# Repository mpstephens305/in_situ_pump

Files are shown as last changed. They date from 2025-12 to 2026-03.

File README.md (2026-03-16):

# in_situ_pump
```diff
-This site is actively under construction and will be fully functional in March, 2026. 
```
<P>A low cost, open source in situ pump for marine and freshwater sampling being developed at Florida International University by Mark Stephens and Andres Martinez.</P>

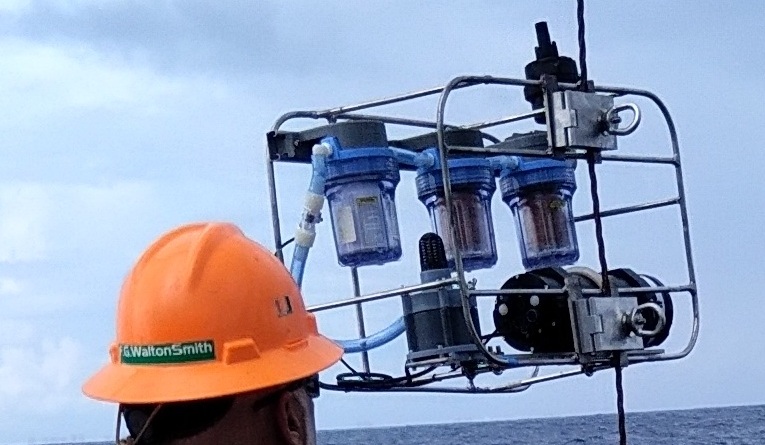
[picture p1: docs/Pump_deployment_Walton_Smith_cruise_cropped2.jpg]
Pump deployment aboard RV Walton Smith in October 2025


<P><b>Motivation: </b>In situ pumps allow for simultaneous sampling at multiple depths. However, commercially available units can cost tens of thousands of dollars. For applications involving shallow deployments, a more feasible solution is desirable. Our intention is to provide a complete step-by-step guide for building, programming, and operating the in_situ_pump. The system is adaptable for use in a variety of environments and projects. Community input and collaborations are most welcome. 
</P>

## Features
* 3D printed pump unit driven by a [Blue Robotics subsea motor](https://bluerobotics.com/store/thrusters/t100-t200-thrusters/m200-motor/).
* Controlled by a [Teensy 4.1](https://www.pjrc.com/store/teensy41.html) development board.
* Electronics and power supply inside watertight enclosure.
* Adaptable to various filter media (cartridges, GFF, acrylic fiber, etc.).
* Adaptable to sampling different chemical and isotopic species in the dissolved and particulate phases in seawater and freshwater.
* Simple operation.
* Easily programmable start delay, sampling duration, and motor speed.

## Fact Sheet:
* Materials cost: ~$2000 US.
* Power supply: c-cell batteries (can be adapted to other batteries including lithium).
* Maximum depth: 300 m.
* Sensors: pressure (depth), temperature, flow rate, voltage, DC current.
* Data storage: microSD card.
* Communications: USB.
* Dimensions: 24 x 18 x 12 in.
* Weight: 40 lb.

## How to Get One

### Hardware
<table>
<TR>
<TD>
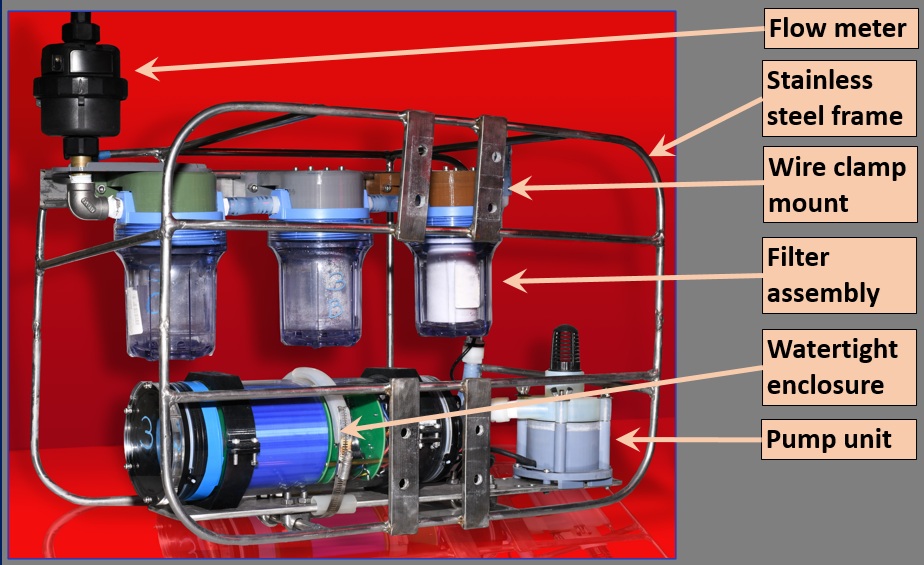
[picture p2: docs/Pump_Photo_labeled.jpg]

	
For step-by-step build instructions for each component, use the following links: <a href="hardware/frame_assembly/frame_assembly.md">frame_assembly</a>, 
<a href="hardware/pump_unit/pump_unit.md">pump_unit_assembly</a>, <a href="hardware/electronics_assembly/electronics_assembly.md">electronics_assembly</a> (including the <a href="hardware/electronics_assembly/pcb_mainboard.md">pcb mainboard_assembly</a> and the <a href="hardware/electronics_assembly/battery_holder_assembly.md">battery_holder_assembly</a>), and the <a href="hardware/filter_holder_assembly/filter_holder_assembly.md">filter_holder_assembly</a>. In addition, we provide CAD files for manufacture of the <a href="hardware/wire_clamp/wire_clamp.md">wire_clamp_assembly</a>. 
</td></tr></table>

### Software
<table width="100%">
	<thead>
    <tr>
      <th width="40%" valign="top"><P>Pump operation is controlled by the Arduino sketch <a href="software/teensy_pump_simple.ino">teensy_pump_simple.ino</P></a>.</P> 
<P>Prior to deployment, the user specifies the pump delay, pump duration, motor speed, and data filename. At the start of a deployment, the program is initialized, and then the countdown to pump start up (i.e., pump delay) begins. The motor then spins up and operates for the specified pump duration.  See the flowchart at the right for the full sequence.</P>
<P>Our step-by-step <a href="software/Software.md">guide</a> includes instructions for software installation, operation, and data recovery.</P>
</th>
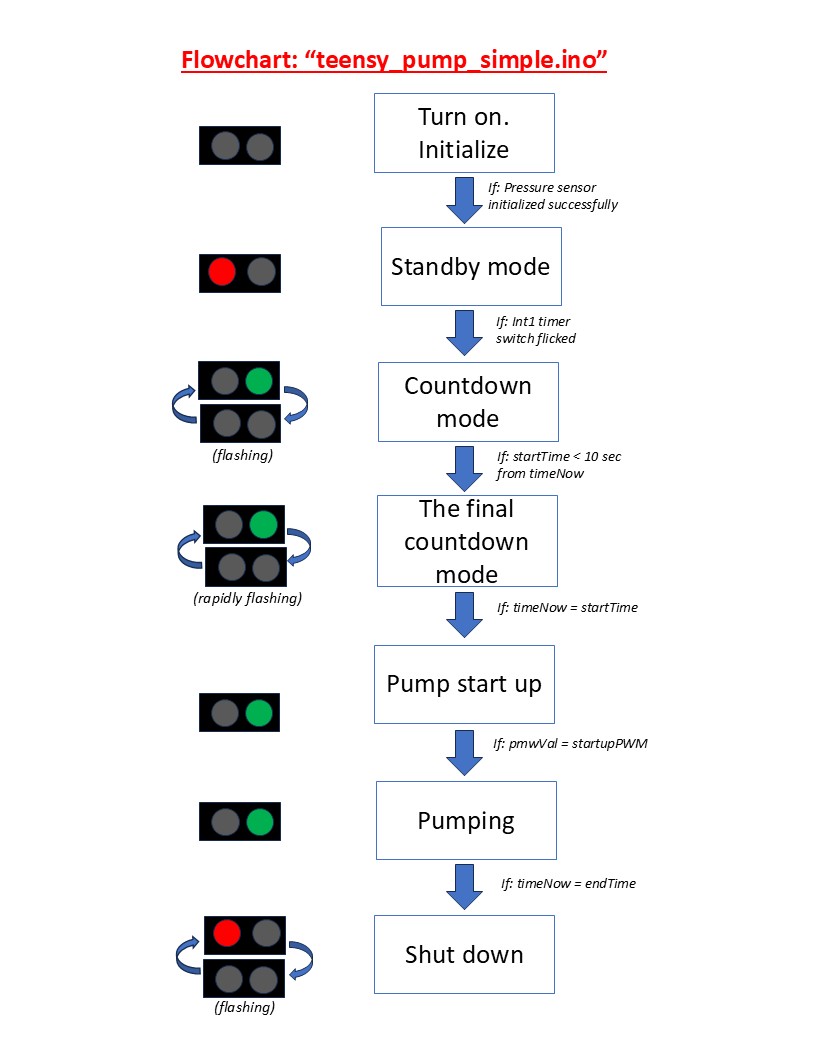
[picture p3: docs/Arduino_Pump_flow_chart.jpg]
      <th width="60%"></th>
    </tr>
  </thead>

</table>

## Deployments

### South Florida Test Cruise
The first ever deployments of the in_situ_pump were conducted in the Gulf Stream offshore South Florida and the Florida Keys on a cruise aboard R/V Walton Smith, October 7-9, 2025. Additional cruises are planned for 2026 in the Sargasso Sea.

<p>A few issues were identified during the this cruise. First, we found that on some deployments the microcontroller repeatedly shut down and rebooted. We identified the issue: the unit was losing power when it swung on the hydrowire during deployment because the springs in the battery compartment were too weak. So, we replaced them with more robust springs.  Second, there were two instances where the outlet of the pump head fractured. In order to address this, we are now using a tougher resin to print these parts. And third, the extraction efficiency of Be-7 from seawater was lower than expected.  In order to address this we are conducting tests using different flow rates and larger masses of filtering material. Additionally, we observed that some of the filter cartridges did not fit snuggly against the filter holders, allowing some of pumped seawater to bypass the filtering material. To address this, we replaced the included gaskets with more robust gaskets of our own design.
	
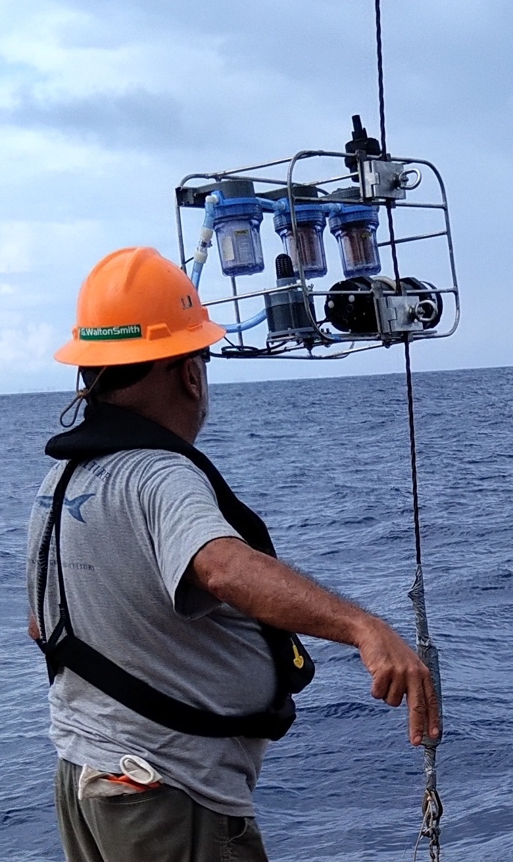
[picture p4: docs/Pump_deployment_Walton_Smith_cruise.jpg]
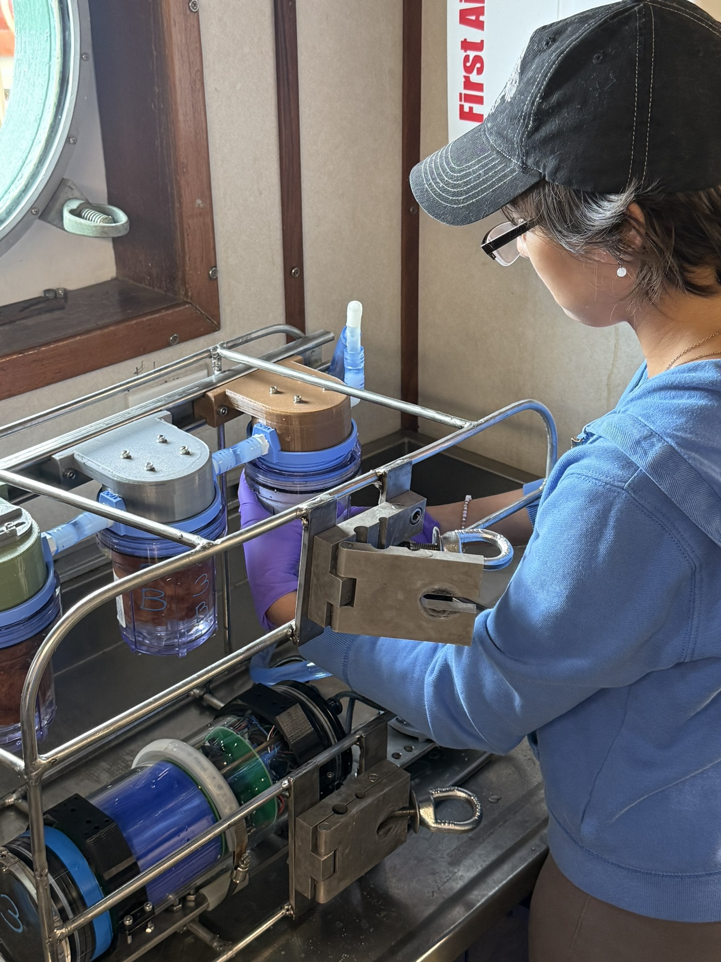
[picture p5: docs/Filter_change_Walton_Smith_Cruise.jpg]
 |  

## Presentations & Publications

### AGU25, New Orleans, 11-19 December 2025

<P>The in_situ_pump was introduced through a poster presentation in <a href="https://macgyver-sessions.github.io/">The MacGyver Sessions</a> at AGU's Annual Meeting. The poster can be accessed via <a href="https://zenodo.org/records/18157174">The MacGyver Sessions Zenodo site</a> as well as on the <a href="https://doi.org/10.22541/essoar.176662276.61585030/v1">ESS Open Archive</a>.

## Acknowledgements
*This project is supported by the U.S.National Science Foundation (Grant # NSF-OCE-2446521). We are grateful for technical support and advice provided at Florida International University's Applied Research Center (FIU-ARC) from the following individuals: Dr Yipeng He, Theophile Pierre, Gabriel Cerioni, and Anthony Abrahao.  Emily Jackson and Sahaira Paz assisted with testing the device and operations on the South Florida cruise. We thank the captain and crew of research vessel F.G. Walton Smith. Photo credits: Emily Jackson and Clint Miller.*

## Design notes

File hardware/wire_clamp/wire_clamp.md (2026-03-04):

# wire_clamp_assembly 

<P>Two wire clamps are used to attach the frame to the hydro wire for deployment.  The book 
clamp design consists of an upper and lower plate that are hinged using a stainless-steel dowel.  
Clamping force is applied by rotating the eye nut onto the threaded rod end bolt.  The design 
includes grooves for two wire sizes.  The dimensions of the clamp body are 3 
x 4.5 x 1.25 inches.  The clamps are attached to the wire clamp mounts on the frame with four 
3/8”-16 stainless steel socket head screws and hex nuts.

<table>
<tr>
<td width="50%">
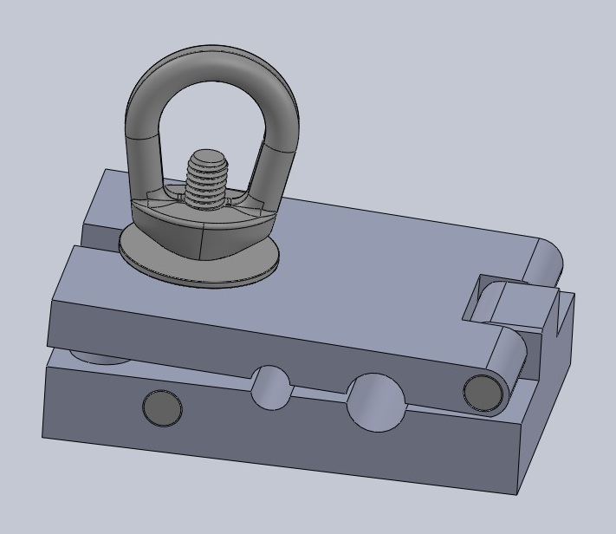
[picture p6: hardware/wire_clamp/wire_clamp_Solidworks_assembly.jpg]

</td>
<td width="50%">
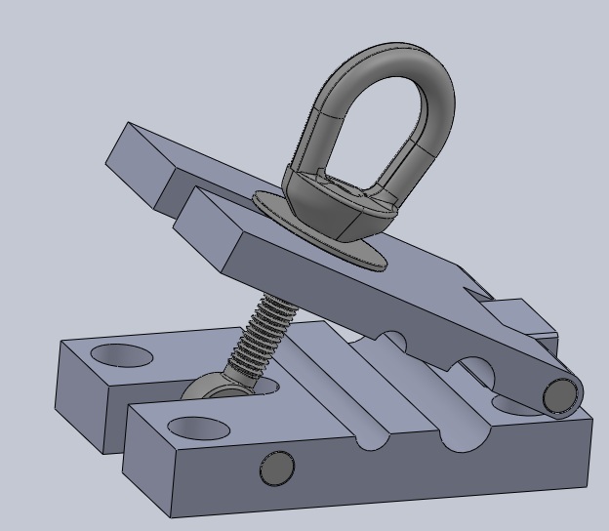
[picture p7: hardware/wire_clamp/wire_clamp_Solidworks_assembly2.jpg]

</td>
</tr>

<tr>
<td colspan=2 align=center>
wire_clamp, Solidworks assembly view
<P>The 3D models including Solidworks parts and assembly are available in the <a href="3D_models/">wire_clamp 3D Models directory</a>.
</td>
</tr>
</table>

<P>
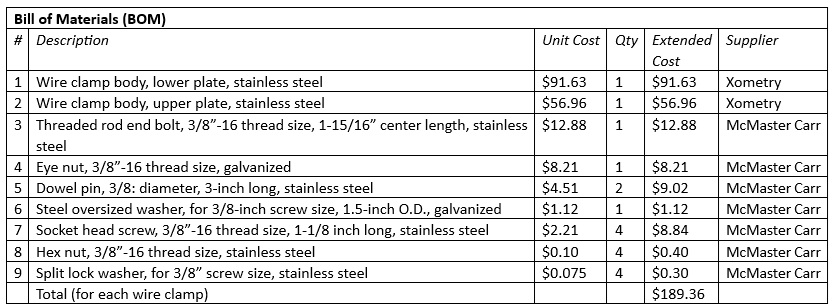
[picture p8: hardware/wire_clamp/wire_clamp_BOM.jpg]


### Assembly (approximate time: 10 minutes):  
1. Attach the lower plate to the wire clamp mounting plates on the frame using four socket head screws, 
hex nuts, and split lock washers. 
2. Attach the upper plate to the lower plate using a stainless-steel dowel. 
3. Attach the threaded rod end bolt to the lower plate using a stainless-steel dowel. 
4.  Place the oversized steel washer and eye bolt onto the threaded rod end bolt. 

### CAD drawings (dimensions in inches):

<table>
<tr>
<td>
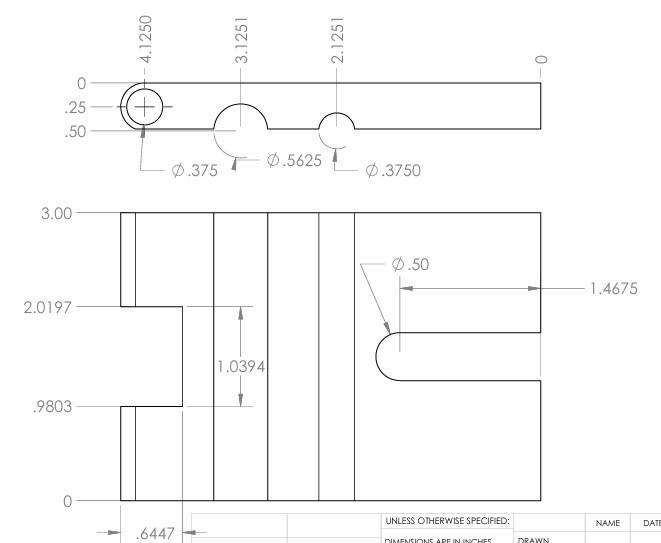
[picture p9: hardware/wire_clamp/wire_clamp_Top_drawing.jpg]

</td>
</tr>
<tr>
<td align=center>
Upper Plate
</td>
</tr>
</table>

<table>
<tr>
<td>
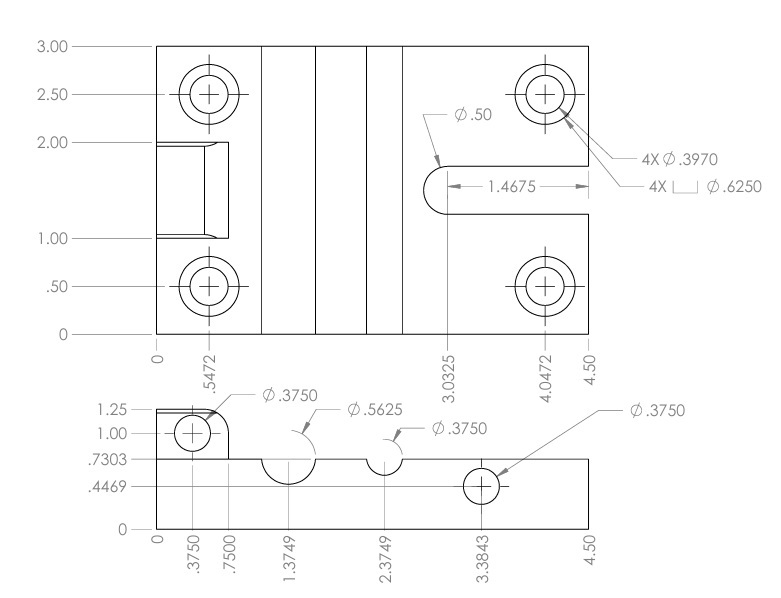
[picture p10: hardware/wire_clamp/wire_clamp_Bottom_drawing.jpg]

</td>
</tr>
<tr>
<td align=center>
Lower Plate
</td>
</tr>
</table>

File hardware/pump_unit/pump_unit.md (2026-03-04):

# pump_unit_assembly
 	 
<P>The pump_unit_assembly consists of a <a href="https://bluerobotics.com/store/thrusters/t100-t200-thrusters/m200-motor/">Blue Robotics M200 subsea motor</a> and 3D printed pump components (<I>pump_base</I>, <I>pump_body</I>, <I>pump_impeller</I>, and <i>pump_head</i>).  The motor is powered by the 14-cell battery pack and controlled by <a href="https://www.pjrc.com/store/teensy41.html">Teensy 4.1</a> via the <a href="https://bluerobotics.com/store/thrusters/speed-controllers/besc30-r3/">Blue Robotics Basic ESC</a>, all of which are contained within the watertight enclosure.  A <a href="https://bluerobotics.com/store/cables-connectors/penetrators/wlp-vp/?attribute_bulkhead-size-seal-size-plug-compression-compatible-cable-diameter=M10+-+6.5+mm+-+LC+-+6.5+mm+%C2%B1+0.3+mm">Blue Robotics WetLink Penetrator</a> links the external motor with the internal power source.  The pump_unit is secured to the frame_baseplate with four M4 stainless steel screws.

<table>
<tr>
<td width=305>
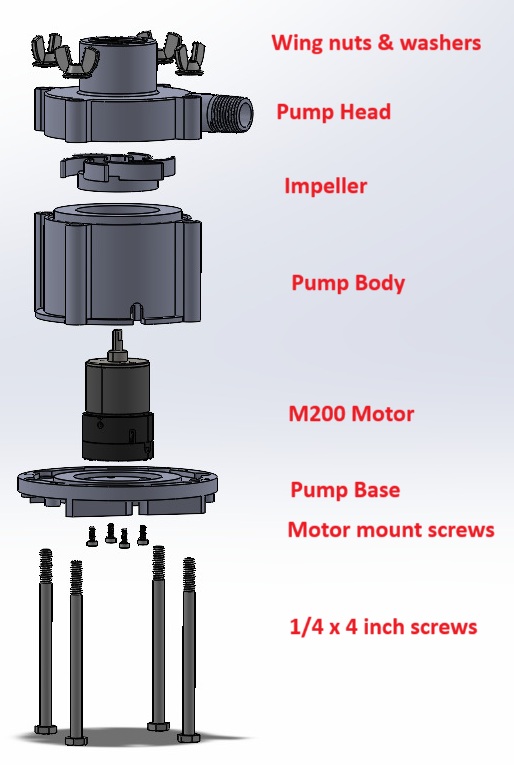
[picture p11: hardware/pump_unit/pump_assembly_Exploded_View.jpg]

</td>
<td width=455>
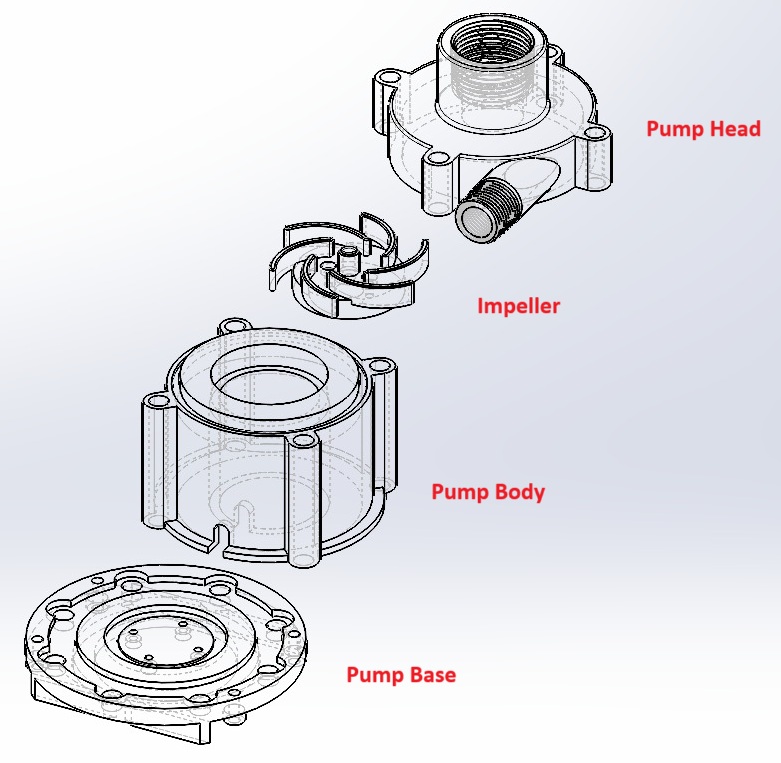
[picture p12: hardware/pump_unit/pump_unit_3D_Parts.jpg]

</td>
</tr>

<tr>
<td align=center>
pump_unit - Exploded View</br>
(Not shown: power cord, strainer, impeller screws, & O-ring)
</td>
<td align=center valign=top>
pump_unit 3D Printed Parts
</td>
</tr>
</table>

<P>
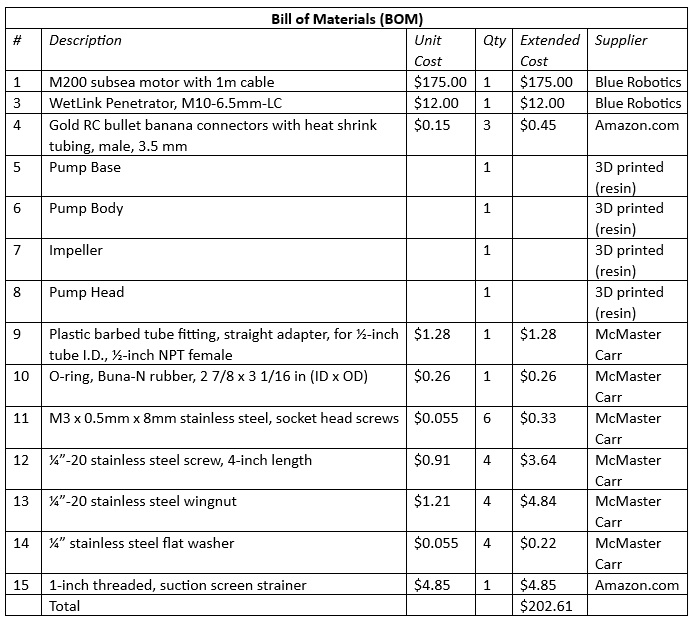
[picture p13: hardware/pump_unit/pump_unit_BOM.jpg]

</P>

### Assembly (approximate time: 20 minutes):  
1. Assemble the WetLink Penetrator with the motor cable following the instructions on the 
Blue Robotics website. 
2. Solder the banana connectors to the three conductors of the motor cable.  Then apply 
heat shrink tubing to the connections. 
3. Attach the motor to pump_base with four M3 x 8mm screws. 
4. Place the pump_body over the motor. 
5. Attach pump_impeller to motor with two M3 x 8mm screws. 
6. Insert O-ring into groove in pump_body. 
7. Seat the pump_head over the pump_impeller and onto pump_body. 
8. Secure pump_head to pump_base with four sets of ¼ inch screws, washers, and 
wingnuts.
9. Screw the 1-inch threaded suction screen strainer into the pump inlet and the 1/2-inch tube fitting onto the outlet.
<table>
<tr>
<td>
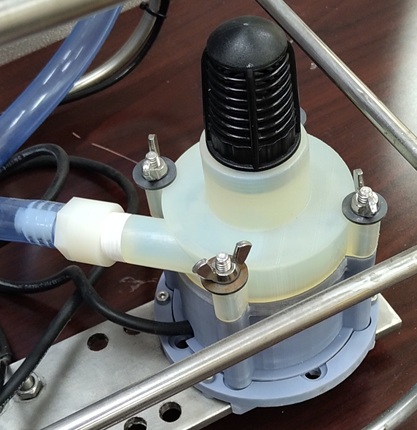
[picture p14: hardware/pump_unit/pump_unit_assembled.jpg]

</td>
</tr>
 <tr>
<td>
Fully assembled pump_unit.
</td>
</tr>
</table>

### 3D Printed Parts
We use a resin printer to produce the pump_unit parts. We have also had success using water resistant filaments, such as PETG, with 100% infill.

The 3D models including .STEP and .STL files are available in the <a href="3D_Models/">3D Models directory</a>.

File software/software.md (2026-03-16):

# software

Given below are step-by-step instructions for A) installing the required software, B) pump operation, and C) data retrieval.

## Installation Instructions

### Step 1: Install *Arduino IDE*
To write the code and upload it to the Teensy 4.1, you will have to use a free software called
Arduino Integrated Development Environment (*Arduino IDE*).
1. Visit https://www.arduino.cc/en/software/ and scroll down until you see Arduino IDE and
download the latest release.
2. Once download finishes, right-click on the file and select “run as administrator”.
3. Follow the pop-ups and select your preferences, then click install.
4. Once installed, open the application.

### Step 2: Install required libraries
To be able to program different components which will be used in the pump, we will need to
install various libraries, Teensyduino to be able to code onto the Teensy board, BlueRobotics
MS5837 Library for the Bar30 pressure sensor, and MTP_Teensy to download the data log after
a run. All the steps below are to be done through the Arduino IDE application.
1. To install Teensyduino, navigate to Files and select preferences.
2. Once the preferences window pops up, you may need to scroll down to even if no
scrollbar appears, in "Additional boards manager URLs" copy the link below then click
OK:
https://www.pjrc.com/teensy/package_teensy_index.json
3. Go back to the main Arduino window and select Boards Manager on the left side.
4. 4. Search Teensy and click install. Now you have the necessary library to operate on the
Teensy.
5. To install the Bar30 pressure sensor library, select Library Manager.
6. 6. Search “BlueRobotics MS5837”.
7. Click install.
8. To install the MTP_Teensy library, visit the link below:
https://github.com/KurtE/MTP_Teensy
9. Click on the green “Code” button and select “Download ZIP”.
10. Once the ZIP file has been downloaded, open your file explorer.
11. Copy the MTP_Teensy file into your Arduino > libraries folder.

### Step 3: Upload Code
The code to run the pump is provided in a .ino file to open on Arduino IDE and upload to the
board. To find this file, go to the GitHub repository, click on the software folder and download
the teensy_pump_simple.ino file. After downloaded, follow the steps below to upload.
1. Connect the cobalt series bulkhead 4-pin cable to the connector on the water tight
enclosure end cap.
2. Open the .ino file with the Arduino IDE application.
3. Select the “Tools” tab on the top left corner of the window.
4. Click on “Board” and select Teensy 4.1.
5. In the same “Tools” tab, click on “Port” and select the correct port corresponding to
where the Teensy is connected.
6. Go back to main window and click “Upload” (the arrow pointing to the right on the top
left of the window).

## Pump operation
The Atrduino sketch <a href="teensy_pump_simple.ino">teensy_pump_simple.ino</a> directs the automatic operation of the pump. Prior to deployment, the user  specifies the following variables: startDelay, pumpTime, startupPWM, and data filename. Then, when the program is activated, pumping begins after startDelay (seconds), operates at a speed corresponding to startupPWM (microseconds), and stops after pumpTime (seconds). Data is recorded every minute to filename.dat.

## Data retrieval
Once you have run the pump you can retrieve data and download it to your computer. The data
includes, date, run time, voltage and current usage, gallons pumped, PWM speed, and depth
(meters).
1. Connect Teensy to your computer through the cobalt series bulkhead 4-pin cable.
2. Select “File” on top left and click “Examples”.
3. Scroll down until you find MTP_Teensy and select mtp-test.
4. Once open, select the “Tools” tab and go to “USB Type”.
5. Select “MTP Disk Experimental”

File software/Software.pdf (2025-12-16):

Software

The software consists of a code which is written on the Arduino IDE and then uploaded to the Teensy 4.1 microcontroller. This code has additional libraries which have to be downloaded to operate some of the components like the Teensy and the Bar30 Pressure Sensor.

The purpose of the code is to run the pump autonomously when turned on at a set speed for the preferred period of time. During the run, it will pump water through the three filters and measure the flow rate.

Download Instructions

Step 1: Installing Arduino IDE

To write the code and upload it to the Teensy 4.1, you will have to use a free software called Arduino IDE.

1. Visit https://www.arduino.cc/en/software/ and scroll down until you see Arduino IDE and download the latest release.
2. Once download finishes, right-click on the file and select “run as administrator”.
3. Follow the pop-ups and select your preferences, then click install.
4. Once installed, open the application.
Step 2: Install required libraries

To be able to program different components which will be used in the pump, we will need to install various libraries, Teensyduino to be able to code onto the Teensy board, BlueRobotics MS5837 Library for the Bar30 pressure sensor, and MTP_Teensy to download the data log after a run. All the steps below are to be done through the Arduino IDE application.

1. To install Teensyduino, navigate to Files and select preferences.
2. Once the preferences window pops up, you may need to scroll down to even if no scrollbar appears, in "Additional boards manager URLs" copy the link below then click OK:
https://www.pjrc.com/teensy/package_teensy_index.json
3. Go back to the main Arduino window and select Boards Manager on the left side.

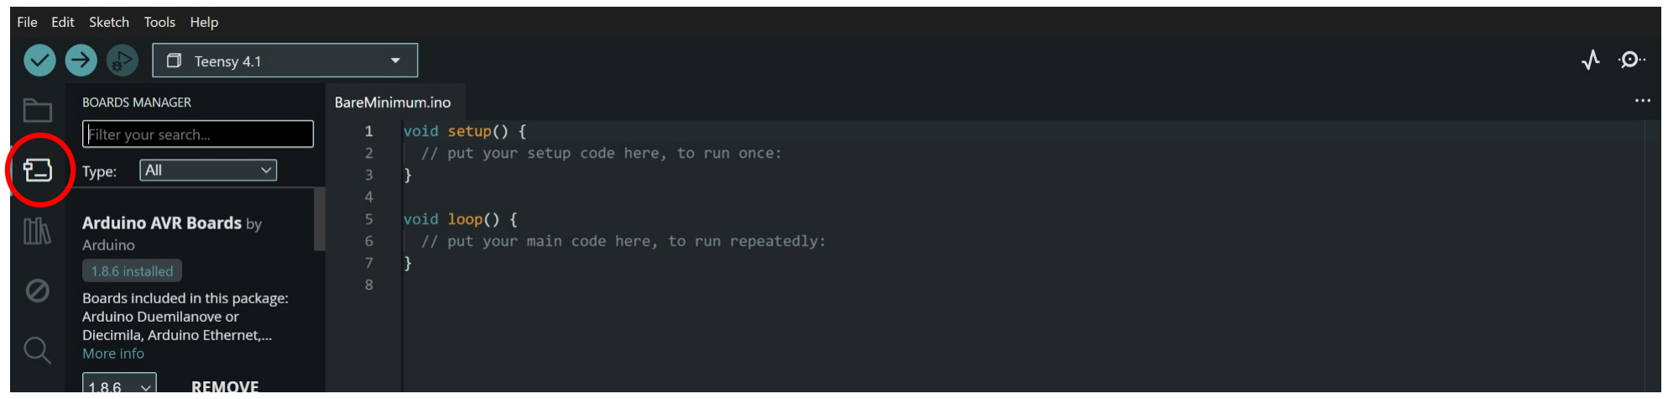
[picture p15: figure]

4. Search Teensy and click install. Now you have the necessary library to operate on the Teensy.
5. To install the Bar30 pressure sensor library, select Library Manager.

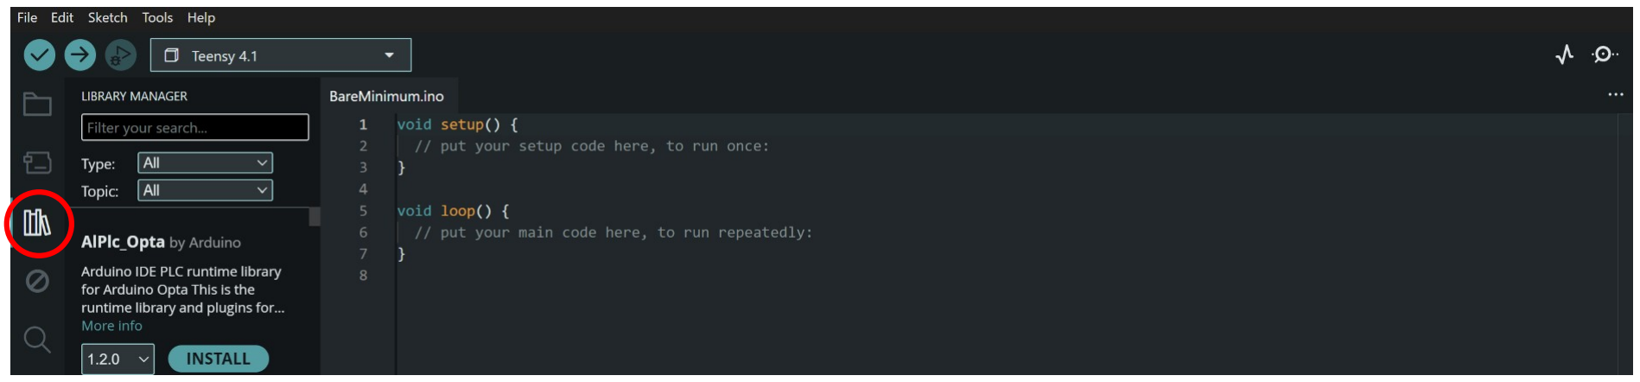
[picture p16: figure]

6. Search “BlueRobotics MS5837”.
7. Click install.
8. To install the MTP_Teensy library, visit the link below: https://github.com/KurtE/MTP_Teensy
9. Click on the green “Code” button and select “Download ZIP”.
10. Once the ZIP file has been downloaded, open your file explorer.
11. Copy the MTP_Teensy file into your Arduino > libraries folder.
Step 3: Upload Code

The code to run the pump is provided in a .ino file to open on Arduino IDE and upload to the board. To find this file, go to the GitHub repository, click on the software folder and download the teensy_pump_simple.ino file. After downloaded, follow the steps below to upload.

1. Connect the cobalt series bulkhead 4-pin cable to the connector on the water tight enclosure end cap.
2. Open the .ino file with the Arduino IDE application.
3. Select the “Tools” tab on the top left corner of the window.
4. Click on “Board” and select Teensy 4.1.
5. In the same “Tools” tab, click on “Port” and select the correct port corresponding to where the Teensy is connected.
6. Go back to main window and click “Upload” (the arrow pointing to the right on the top left of the window).
Step 4: Retrieving Data

Once you have run the pump you can retrieve data and download it to your computer. The data includes, date, run time, voltage and current usage, gallons pumped, PWM speed, and depth (meters).

1. Connect Teensy to your computer through the cobalt series bulkhead 4-pin cable.
2. Select “File” on top left and click “Examples”.
3. Scroll down until you find MTP_Teensy and select mtp-test.
4. Once open, select the “Tools” tab and go to “USB Type”.
5. Select “MTP Disk Experimental”

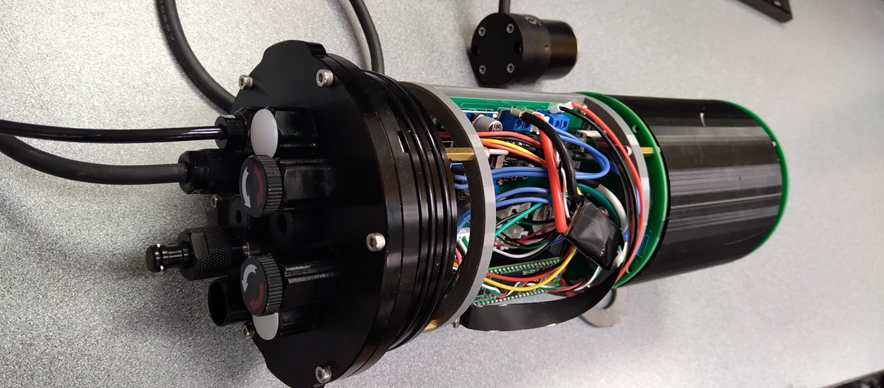
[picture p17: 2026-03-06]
hardware/electronics_assembly/Images/end_cap_and_electronics.jpg

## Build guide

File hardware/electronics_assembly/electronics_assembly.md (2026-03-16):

# electronics_assembly
 	 
The electronics_assembly includes PCB_mainboard and the battery_holder_assembly, which are contained within a Blue Robotics watertight enclosure with locking endcaps. Mounted on one end cap are two LED indicators, two switches, and the pressure sensor, as well as penetrators for external components including the M200 motor, USB, and optional flow sensors. The other end cap gives access to the the battery holder.  The assembly is clamped to the frame’s base plate. 
<P>Separate pages give detailed instructions for assembling <a href="pcb_mainboard.md">PCB mainboard</a> and the <a href="battery_holder_assembly.md">battery_holder_assembly</a>.

 <P>
  <table>
    <tr>
      <td align=center>
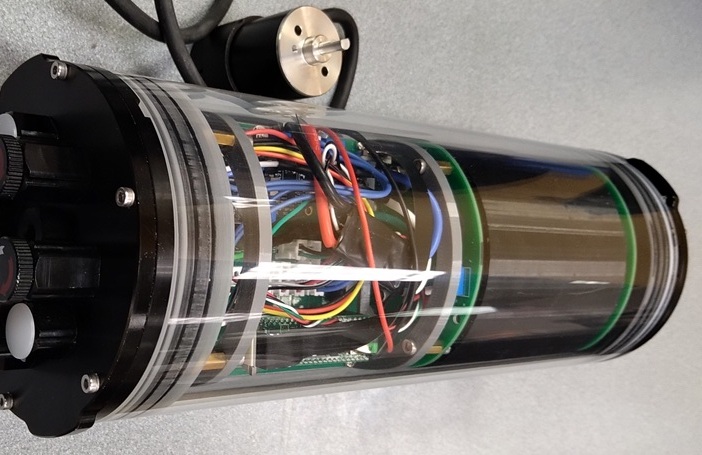
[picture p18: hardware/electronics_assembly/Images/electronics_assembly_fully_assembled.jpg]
        
      </td>
    </tr>
    <tr>
      <td align=center>
        electronics_assembly, fully assembled.
      </td>
    </tr>
  </table>
</P>

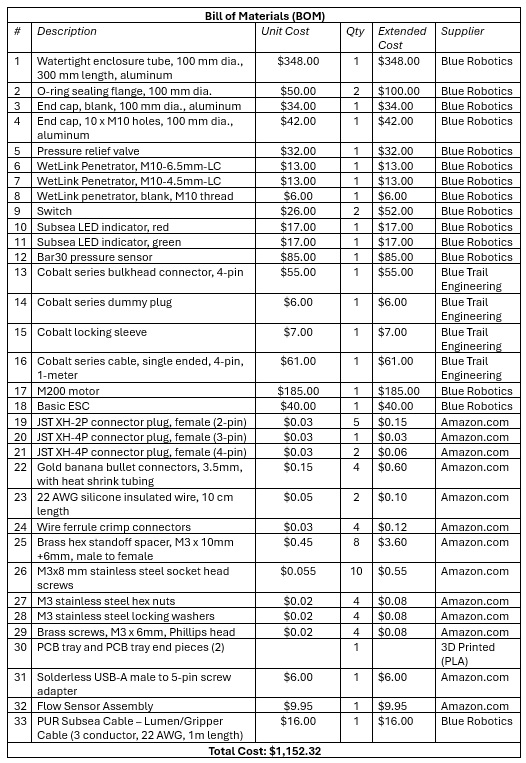
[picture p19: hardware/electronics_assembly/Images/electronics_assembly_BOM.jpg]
<P></P>

## Assembly (approximate time: 2 hours):  
> [!IMPORTANT]
> **Recommended tools and supplies**: Blue Robotics WetLink Bulkhead Wrench, adjustable wrench, bench vise, wire strippers, and ratcheting crimping tools for JST connectors and wire ferrules.
> <P>Separate pages give detailed instructions for assembling <a href="pcb_mainboard.md">PCB mainboard</a> and the <a href="battery_holder_assembly.md">battery_holder_assembly</a>.

1. Attach the endcaps to the O-ring sealing flanges using the included face seal O-ring and end cap screws. 
2. Prepare each wire by trimming it to ≈ 10cm, stripping the end, and crimping on a female pin connector. The plastic JST connector bodies should be attached according to the wiring guide below.
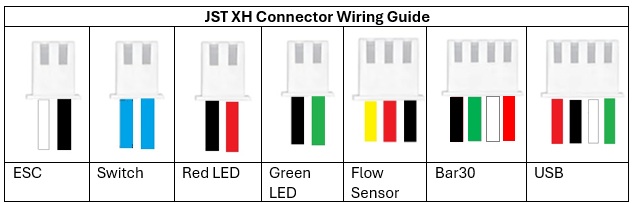
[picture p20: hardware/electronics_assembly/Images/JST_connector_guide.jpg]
<P></P>

> [!TIP]
> The assembled 3-pin and 4-pin connectors will not fit through the M10 end cap holes. Therefore, it is recommended not to insert the wires into the plastic body until the component or cable penetrator has been mounted to the end cap.

3. Mount the following components to the M10 x10 hole end cap: WetLink penetrators for the motor and flow sensor, Bar30 pressure sensor, red and green LEDs, two switches, Cobalt bulkhead connector (USB), pressure relief valve, and a blank penetrator.

  <P>
  <table>
    <tr>
      <td align=center>
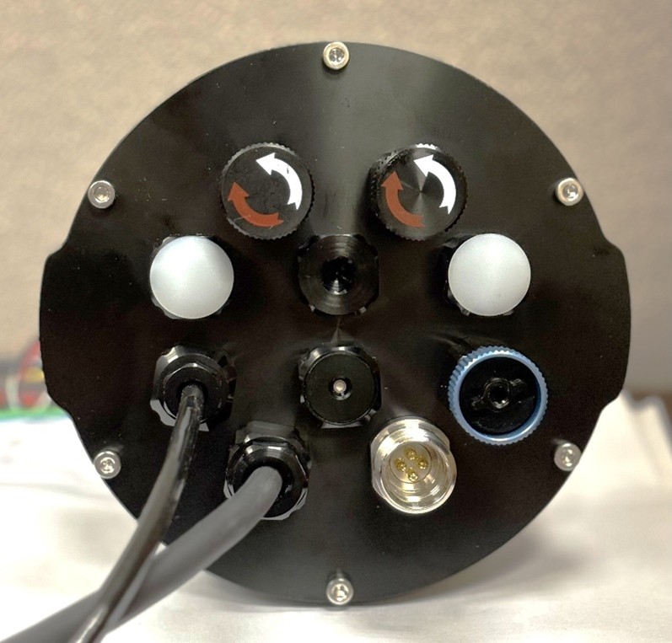
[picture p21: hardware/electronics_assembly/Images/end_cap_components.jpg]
        
      </td>
     <td align=center>
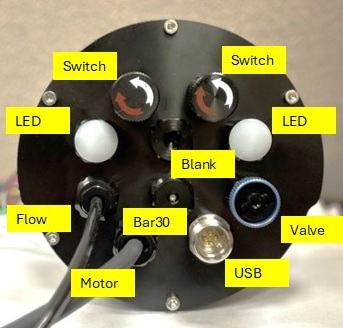
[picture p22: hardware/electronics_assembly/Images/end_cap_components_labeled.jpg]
        
      </td>
    </tr>
    <tr>
      <td align=center colspan=2>
        M10 x10 hole end cap with mounted components.
      </td>
    </tr>
  </table>
</P>

4. Assemble the PCB_tray using one M3x8mm socket head screw on each end, and attach the assembled PCB_mainboard using M3x8mm screws through the four mounting holes.

<P>
  <table>
    <tr>
      <td align=center>
        
      </td>
    </tr>
    <tr>
      <td align=center>
        PCB tray with mainboard PCB.
      </td>
    </tr>
  </table>
</P>

5. Screw four M3x10mm brass hex spacers into the mounting holes in the sealing flange, and then attach the PCB_tray to the spacers using M3x8mm socket head screws and locking washers.
6. Plug in the following components to the assembled PCB_mainboard: red and green LEDs, two switches, Bar30 Pressure sensor, Cobalt connector wires (USB connection), Flow sensor, and ESC connector.
7. Insert the ESC power leads (thick red and black wires) into the ESC screw terminal block on the PCB, and tighten the screws down.
8. Solder banana connectors to the three conductors of the motor cable (male) and ESC (female).  Then apply heat-shrink tubing over the connectors.
9. Insert the three banana connector male leads from the M200 motor into the matching color female leads from the ESC.
10. Prepare 10cm lengths of red and black 22 awg wire, strip the ends, and then crimp a ferrule to each wire end.
11. Insert ferrules into screw terminals on the PCB_mainboard (terminal labeled 'Battery') and the assembled battery holder bottom PCB, and tighten down.
12. Attach four M3x10mm brass hex spacers to the PCB_tray end using a nut and locking washer, and then attach the battery holder bottom PCB to the brass spacers using M3x6mm phillips head brass screws.
13. Assemble the rest of the battery_holder_assembly (instructions <a href="battery_holder_assembly.md">here</a>).
14. The assembly can now be inserted into the cylindrical watertight enclosure and locked into place with the provided locking cord.
15. Finally, assemble the blank end cap with its o-ring sealing flange and attach it to the watertight enclosure (note: loosen the pressure valve to insert the flange / end-cap).

<P>
  <table>
    <tr>
      <td align=center rowspan=4>
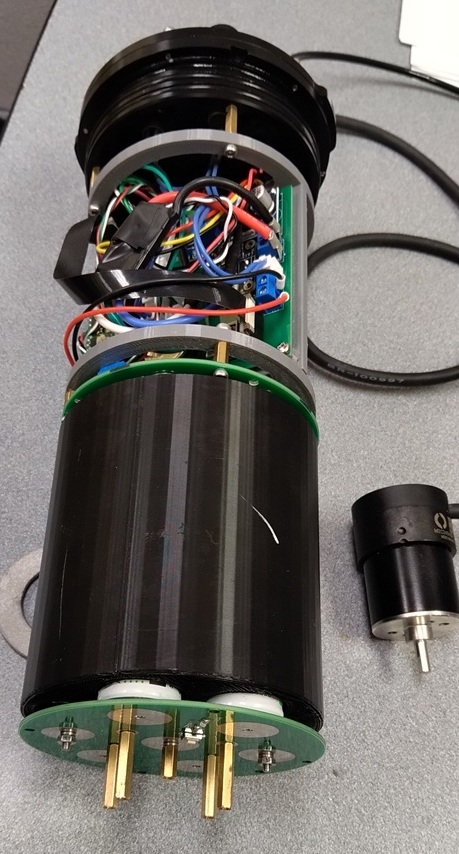
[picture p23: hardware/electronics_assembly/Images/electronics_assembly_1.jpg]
        
      </td>
      <td align=center valign=bottom>
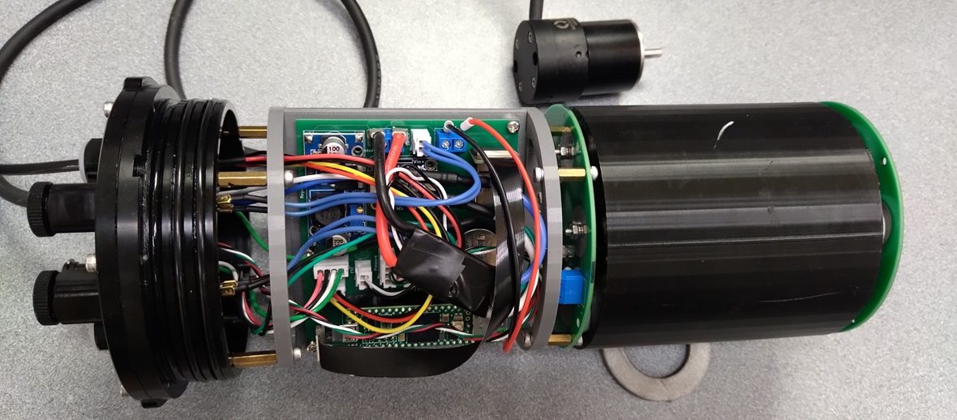
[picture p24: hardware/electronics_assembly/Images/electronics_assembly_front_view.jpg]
        
      </td>
    </tr>
    <tr>
      <td align=center>
        PCB tray front view.
      </td>
    </tr>
    <tr>
     <td align=center valign=bottom>
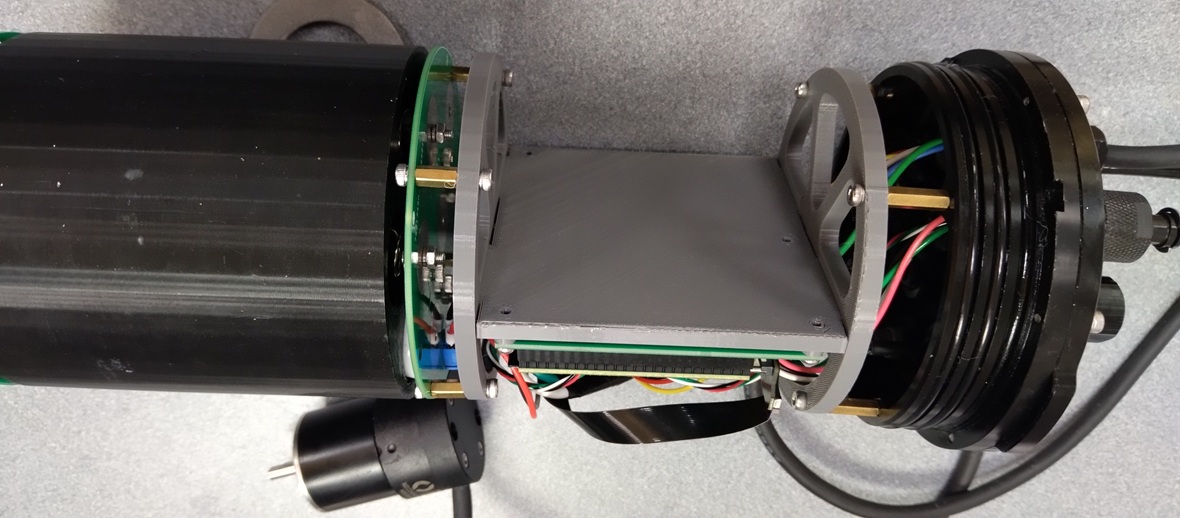
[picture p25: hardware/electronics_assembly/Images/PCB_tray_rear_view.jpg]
        
      </td>
    </tr>
   <tr>
     <td align=center>
        PCB tray rear view.
      </td>
    </tr>
  </table>
</P>

### Data cable
To assemble the USB data cable, first strip the ends of the four leads on the Cobalt Series cable and then attach them to the USB-A male to 5-pin screw adapter as shown below. 
<P>
  <table>
    <tr>
      <td align=center>
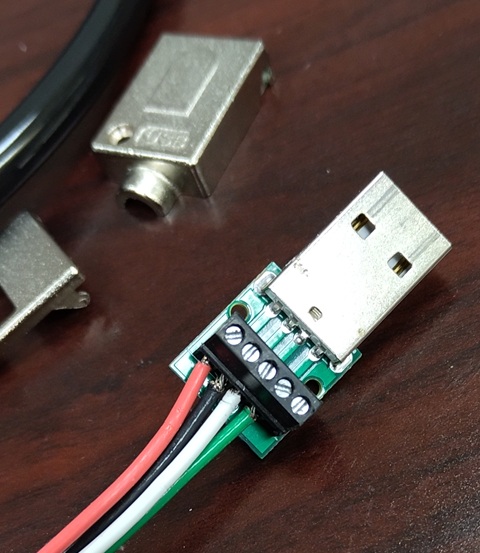
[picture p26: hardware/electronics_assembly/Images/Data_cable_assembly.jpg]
        
      </td>
      <td align=center>
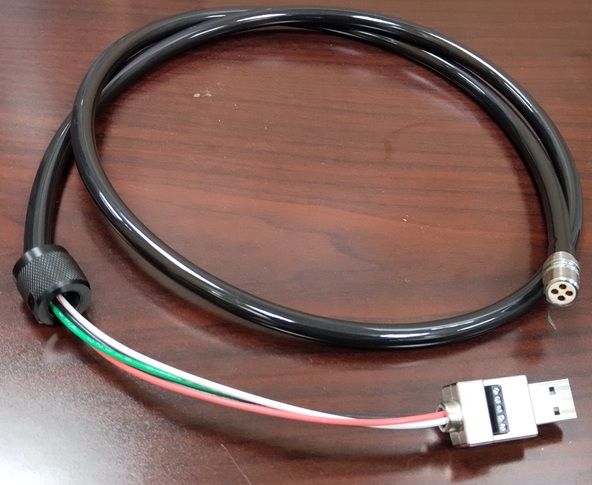
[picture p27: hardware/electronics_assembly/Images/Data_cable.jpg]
        
      </td>
    </tr>
  </table>
  
### 3D Printed Parts
We print the PCB tray using PLA filament. The 3D model files are available in the [3D models directory](3D_Models/).
<P>
  <table>
    <tr>
      <td align=center>
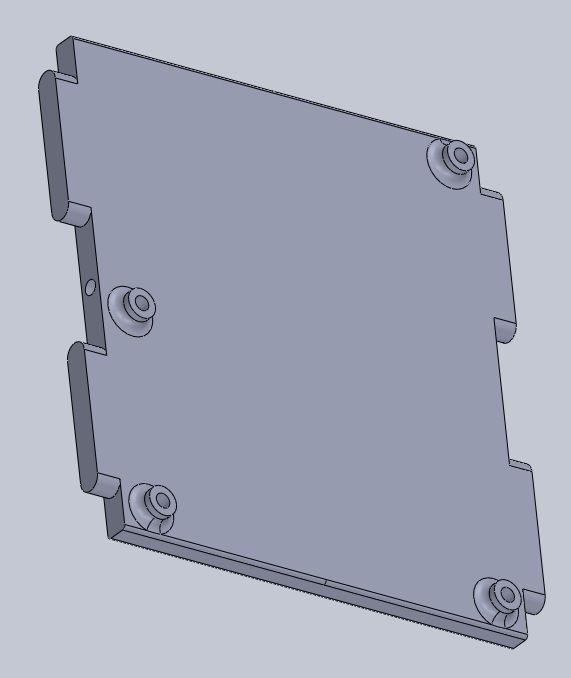
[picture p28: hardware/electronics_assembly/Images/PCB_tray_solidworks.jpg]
        
      </td>
      <td align=center>
        
      </td>
    </tr>
    <tr>
      <td align=center>
        PCB tray.
      </td>
     <td align=center>
        PCB tray end piece.
      </td>
    </tr>
  </table>
</P>

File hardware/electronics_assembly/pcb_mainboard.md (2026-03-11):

# pcb_mainboard
 	 
pcb_mainboard contains the [Teensy 4.1](https://www.pjrc.com/store/teensy41.html) microprocessor and connections for external components including the motor electronic speed controller (ESC), pressure sensor, switches and LEDs, and the USB port. A Buck converter module regulates the voltage supplied to Teensy (5V). A coin cell battery holder powers Teensy’s real time clock (RTC) when the unit is powered down. Teensy’s built-in microSD card slot allows for data logging. Optional components include an INA219 current sensor (to monitor amps consumed by the motor) and two Hall effect flowmeter connections. pcb_mainboard is mounted on the pcb_tray_part via four mounting holes.  
<P><table>
<tr>
<td width=400>
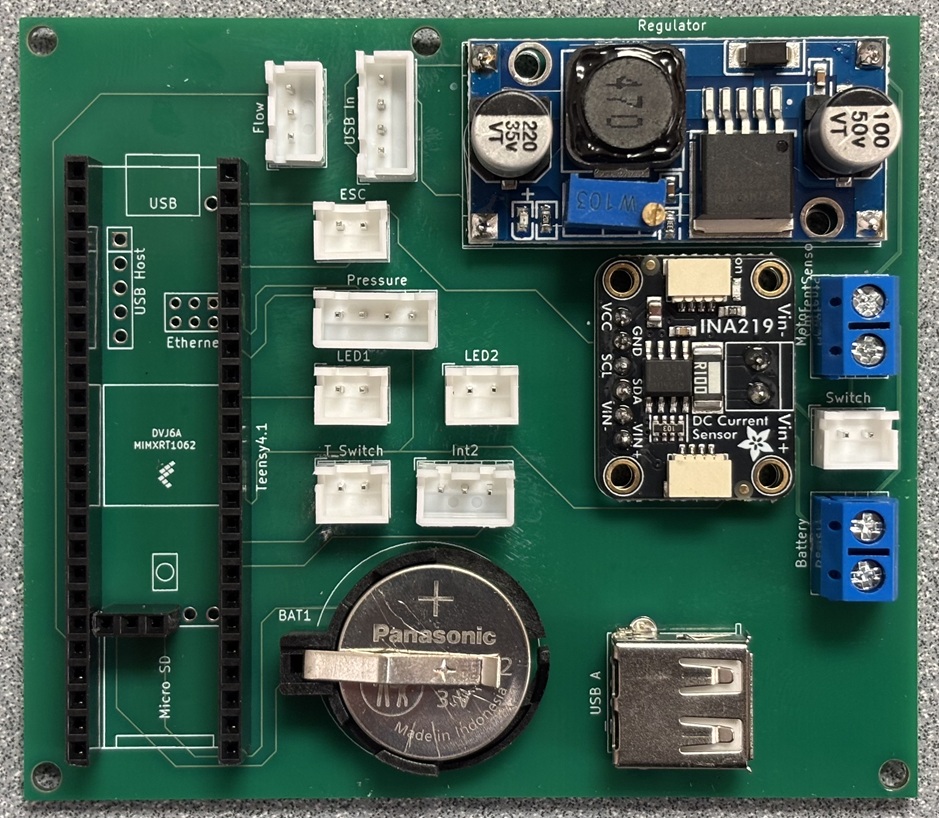
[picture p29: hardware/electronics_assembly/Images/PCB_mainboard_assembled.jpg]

</td>
<td width=400>
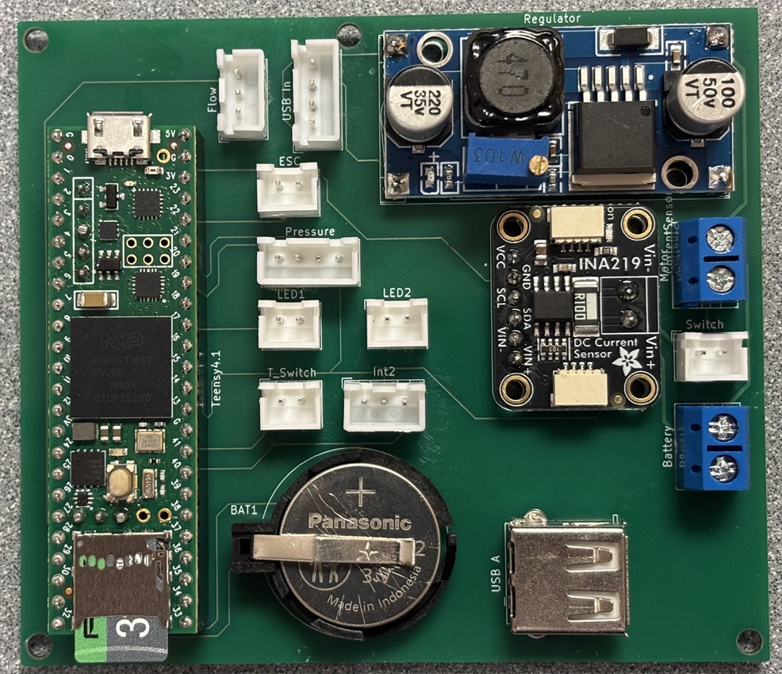
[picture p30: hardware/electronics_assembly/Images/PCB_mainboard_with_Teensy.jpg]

</td>
</tr>
<tr>
<td align=center>
Assembled pcb_mainboard
</td>
<td align=center valign=top>
Assembled pcb_mainboard with with Teensy 4.1
</td>
</tr>
</table></p>

## Assembly (approximate time: 45 minutes):  
> [!IMPORTANT]
> * Refer to the photos above to ensure components are oriented correctly.

1.	Solder pin headers for Teensy 4.1 to the PCB.
2.	Solder battery holder, JST-XH connectors, screw terminal block connectors, voltage regulator, USB-A socket, and current sensor (optional) to the PCB.
3.	Using an external power supply or the battery_holder_assembly to power to the Buck converter, adjust the output to 5V.
4.	Insert Teensy 4.1 with Micro SD into headers.
5.	Connect the USB-A socket to Teensy's microUSB socket using the ribbon USB cable.
6.	Insert coin battery.

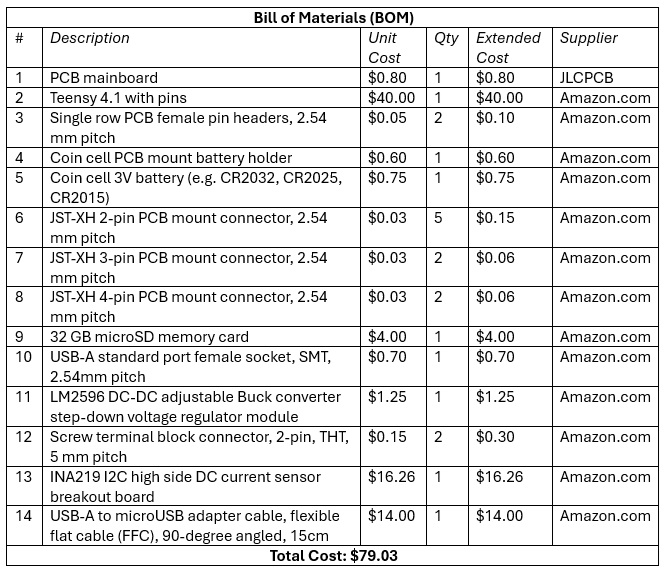
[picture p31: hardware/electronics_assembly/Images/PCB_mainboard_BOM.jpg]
<P></P>

### Gerber files
Gerber files for PCB production can be found in the <a href="Gerbers/">Gerber files directory</a>.
<P><table>
<tr>
<td width=355>
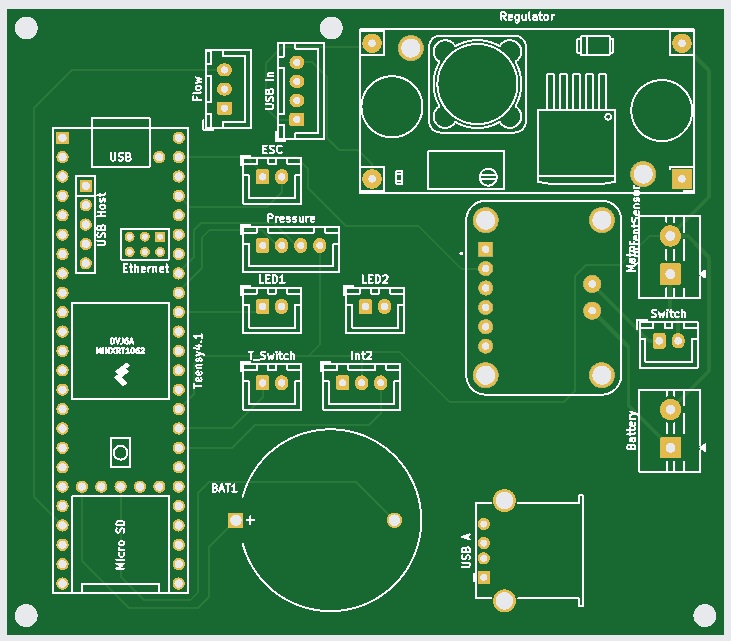
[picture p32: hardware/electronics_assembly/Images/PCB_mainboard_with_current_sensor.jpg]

</td>
<td width=355>
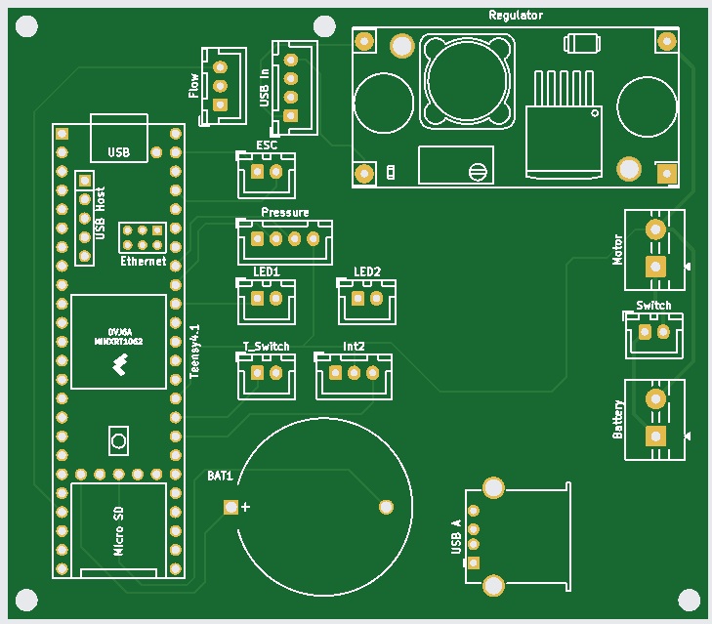
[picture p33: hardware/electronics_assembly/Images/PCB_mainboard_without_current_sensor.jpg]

</td>
</tr>
<tr>
<td align=center>
PCB mainboard with current sensor
</td>
<td align=center valign=top>
PCB mainboard without current sensor
</td>
</tr>
</table></p>

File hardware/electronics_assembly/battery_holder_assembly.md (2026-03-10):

# battery_holder_assembly

<P>The battery_holder_assembly consists of a 3D printed battery holder tube sandwiched between two PCBs (the battery holder top and bottom PCBs). The holder accomodates 14 c-cell batteries.  Alkaline or rechargeable NiMH batteries may be used. The unit is held together by four 135mm stainless steel socket head screws that pass through holes in the PCBs (two blank holes and two vias).  The screws fastened through the vias create a conductive pathway between the top and bottom PCBs.  
</p>

<P><table>
<tr>
<td width=355>
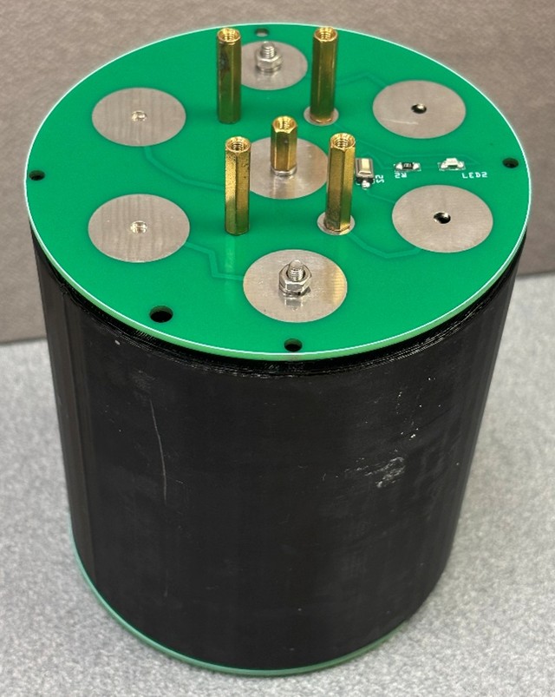
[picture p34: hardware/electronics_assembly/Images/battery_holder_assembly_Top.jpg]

</td>
<td width=355>
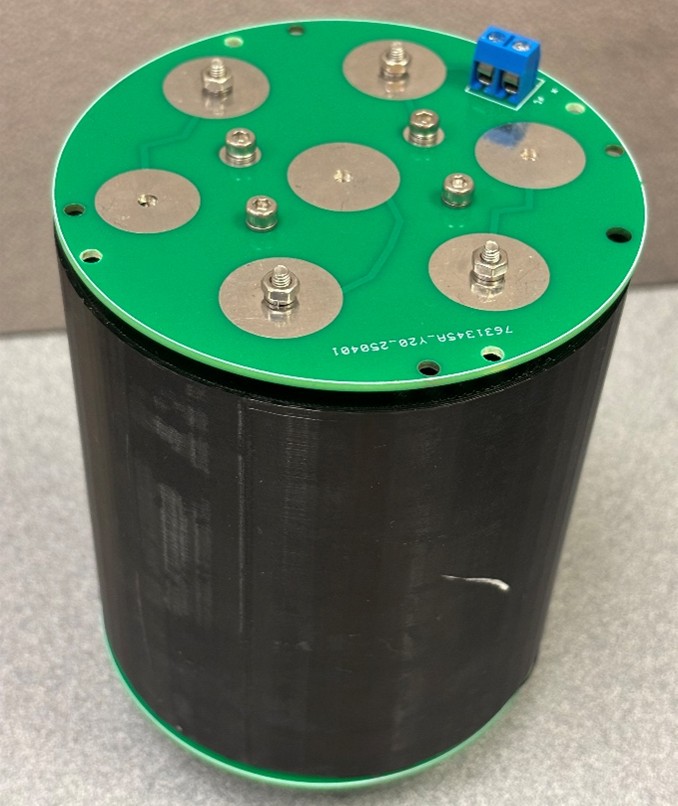
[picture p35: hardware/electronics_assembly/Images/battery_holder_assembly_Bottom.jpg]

</td>
</tr>
<tr>
<td align=center>
battery_holder_assembly top
</td>
<td align=center valign=top>
battery_holder_assembly bottom
</td>
</tr>
</table></p>

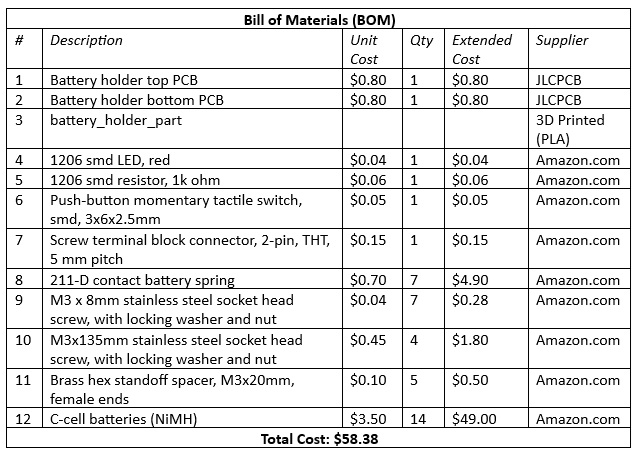
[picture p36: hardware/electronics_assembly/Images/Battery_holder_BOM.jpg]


### Assembly (approximate time: 30 minutes): 
1. Assemble the battery holder top and bottom PCBs (scroll down for PCB assembly instructions).
1.	Attach four M3x135 mm socket head screws with washers and nuts through the bottom PCB, as shown in the photo below.
<P>
  <table>
    <tr>
      <td>
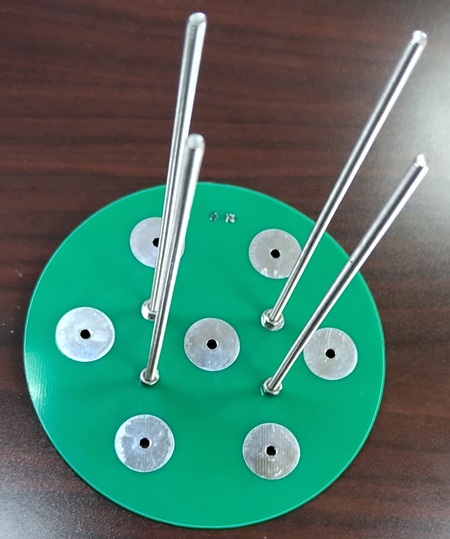
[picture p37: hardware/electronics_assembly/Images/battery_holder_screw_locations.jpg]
        
      </td>
    </tr>
    <tr>
      <td align=center>
        Insert 135 mm screws through bottom PCB.
      </td>
    </tr>
  </table>
</P>
2.	Pass the screws through the four holes in the battery holder tube and load the tube with 14 C cell batteries.
<P>
  <table>
    <tr>
      <td align=center>
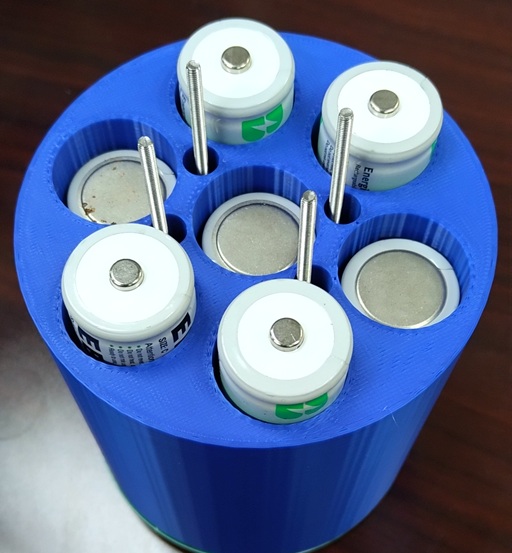
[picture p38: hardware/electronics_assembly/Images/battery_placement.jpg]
        
      </td>
    </tr>
    <tr>
      <td align=center>
        Slide the battery_holder_part over the 135mm screws and insert batteries.
      </td>
    </tr>
  </table>
</P>
3. Pass the ends of the 135mm screws through the holes in the assembled top PCB and fasten the PCB down using four 20mm brass hex spacers. Note that the PCBs must be lined up such that the screws pass through the corresponding vias in both PCBs.

### PCB: Battery Holder Top
<P>The assembled batter_holder_top PCB includes a push button and red LED to check for proper assembly and battery strength.</P>

#### Assembly (approximate time: 15 minutes): 
1.	Solder the LED, switch, and resistor to board.
2.	Attach three springs to middle row of conductor pads (i.e., the large vias) using M3x8mm screws, locking washers, and nuts.
3.	For the center hole, an M3x20mm hex brass spacer, used in place of a nut, serves as a handle for removing the PCB during battery replacement.
<P><table>
<tr>
<td width=355>
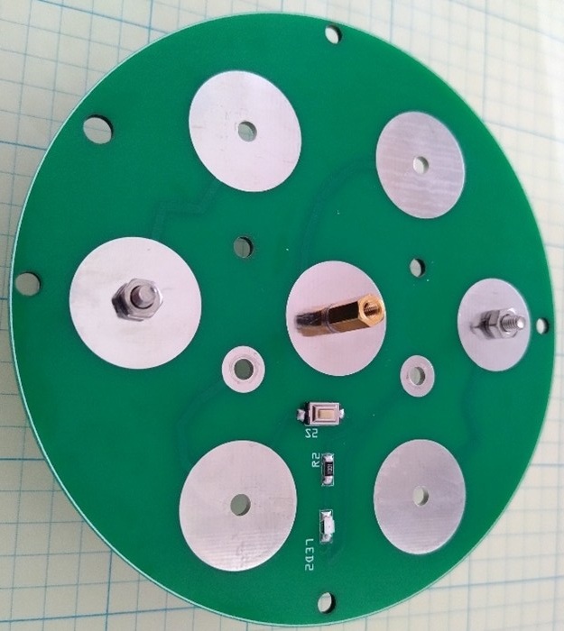
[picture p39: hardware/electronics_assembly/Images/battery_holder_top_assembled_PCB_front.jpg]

</td>
<td width=355>
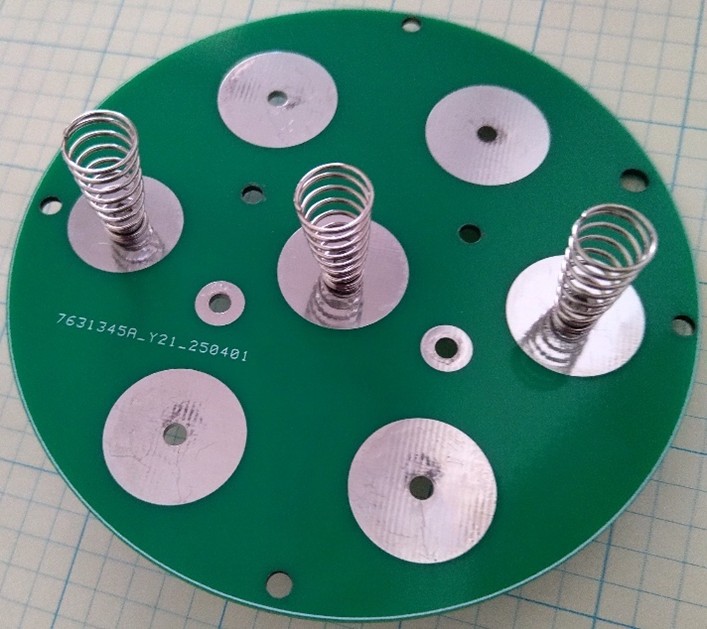
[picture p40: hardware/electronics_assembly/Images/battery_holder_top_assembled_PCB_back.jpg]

</td>
</tr>
<tr>
<td align=center>
Battery holder top assembled PCB (front view)
</td>
<td align=center valign=top>
Battery holder top assembled PCB (back view)
</td>
</tr>
</table></p>

### PCB: Battery Holder Bottom
 	 
<P>The assembled battery_holder_bottom PCB includes a screw terminal block connector for power output to pcb_mainboard and the motor. Four holes along the perimeter of the PCB allow it ot be mounted above pcb_mainboard using brass hex spacers and screws.</P>

#### Assembly (approximate time: 15 minutes): 
1.	Solder the screw terminal to the board.
2.	Attach four springs to conductive pads (i.e., large vias using M3x8mm screws, locking washers, and nuts (see photos below).
<P><table>
<tr>
<td width=355>
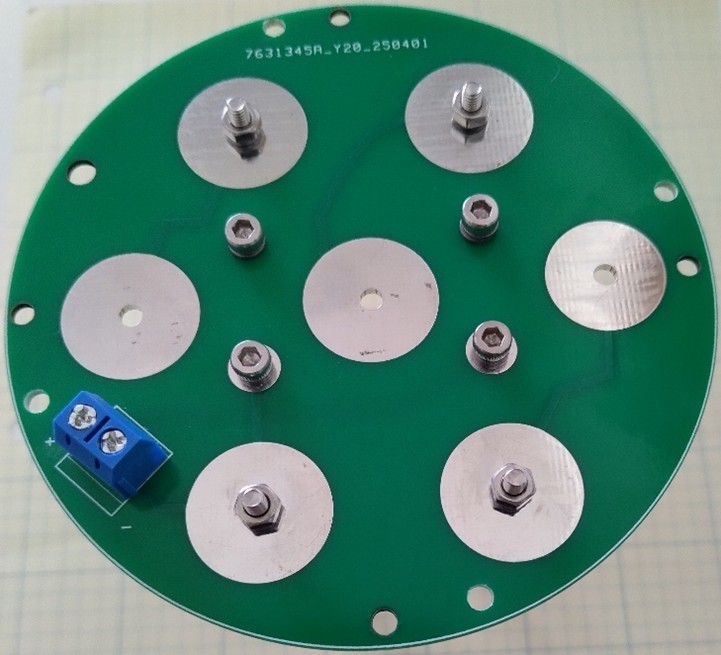
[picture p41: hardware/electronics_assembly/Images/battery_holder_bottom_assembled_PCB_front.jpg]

</td>
<td width=355>
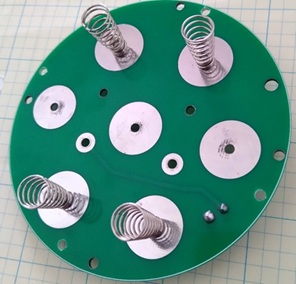
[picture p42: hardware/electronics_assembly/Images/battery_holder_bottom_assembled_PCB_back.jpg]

</td>
</tr>
<tr>
<td align=center>
Battery holder bottom assembled PCB (front view)
</td>
<td align=center valign=top>
Battery holder bottom assembled PCB (back view)
</td>
</tr>
</table></p>

### 3D Printed Parts & Gerber Files
We use PLA filament to produce the battery_holder_part. The 3D models (C-cells_105mm) are available in the <a href="3D_Models/">3D Models directory</a>.
<P>Gerber files for PCB production can be found in the <a href="Gerbers/">Gerber files directory</a></P>
<P>
  <table>
    <tr>
      <td>
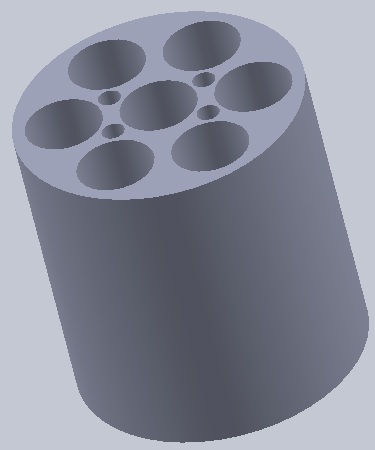
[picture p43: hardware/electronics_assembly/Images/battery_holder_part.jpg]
        
      </td>
    </tr>
    <tr>
      <td align=center>
        battery_holder_part
      </td>
    </tr>
  </table>
</P>
<P><table>
<tr>
<td width=355>
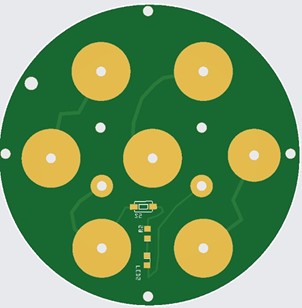
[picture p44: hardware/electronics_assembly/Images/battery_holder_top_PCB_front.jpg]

</td>
<td width=355>
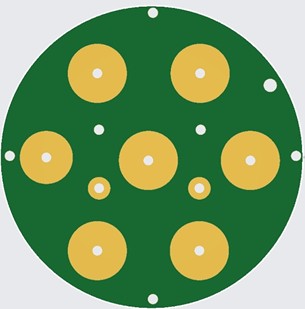
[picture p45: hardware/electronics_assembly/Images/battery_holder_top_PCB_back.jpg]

</td>
</tr>
<tr>
<td align=center>
Battery holder top PCB (front view)
</td>
<td align=center valign=top>
Battery holder top PCB (back view)
</td>
</tr>
</table></p>
<P><table>
<tr>
<td width=355>
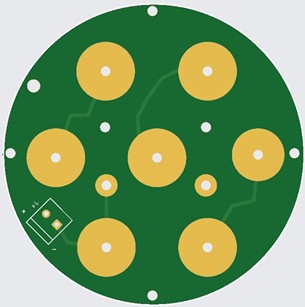
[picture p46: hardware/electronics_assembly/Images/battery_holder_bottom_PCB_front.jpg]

</td>
<td width=355>
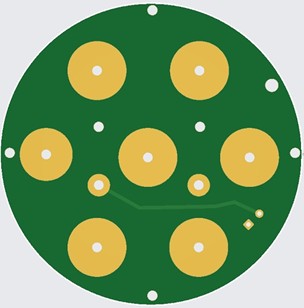
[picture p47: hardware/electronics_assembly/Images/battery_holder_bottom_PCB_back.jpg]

</td>
</tr>
<tr>
<td align=center>
Battery holder bottom PCB (front view)
</td>
<td align=center valign=top>
Battery holder bottom PCB (back view)
</td>
</tr>
</table></p>

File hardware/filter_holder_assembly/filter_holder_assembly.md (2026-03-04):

# filter_holder_assembly
The filter_holder_assembly provides a way to secure the filter holders to the frame_assembly. 
<p>Our setup, designed for Beryllium-7 sampling, includes three <a href="https://www.pentair.com/en-us/water-treatment-components/filter-housings/traditional_slim_line_series.html">Pentek Slim Line 5-inch filter holders</a> in series. The first holder contains a 1-micron drop-in water filter to capture particulates, and the next two holders contain iron-impregnated acrylic fibers contained within refillable filter cartidges sold by <a href="https://www.bulkreefsupply.com/mini-brs-reactor-refillable-cartridge-hard-shell.html">Bulk Reef Supply</a>. Seawater is pushed through the three filters by the pump_unit_assembly and exits through a mechanical flow meter from <a href="https://assuredautomation.com/WM-PD/">Assured Automation</a>.
<P>The design is readily adaptable to accomodate other sampling needs. For example, the suction end of the pump_unit_assembly can be attached to the end of the filter series to pull rather than push water through the filters. It can also be adapted for other filter types (e.g. GF/F) and filter holders.

<P>
   <table>
      <tr>
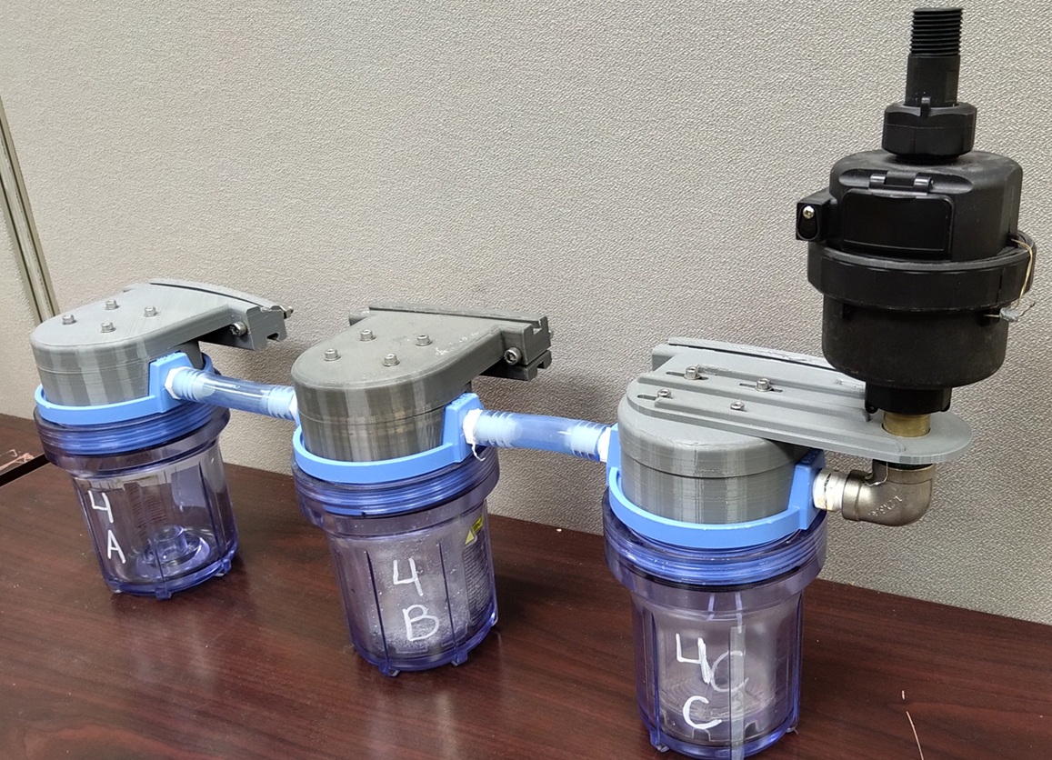
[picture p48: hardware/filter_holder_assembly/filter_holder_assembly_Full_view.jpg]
         <td></td>
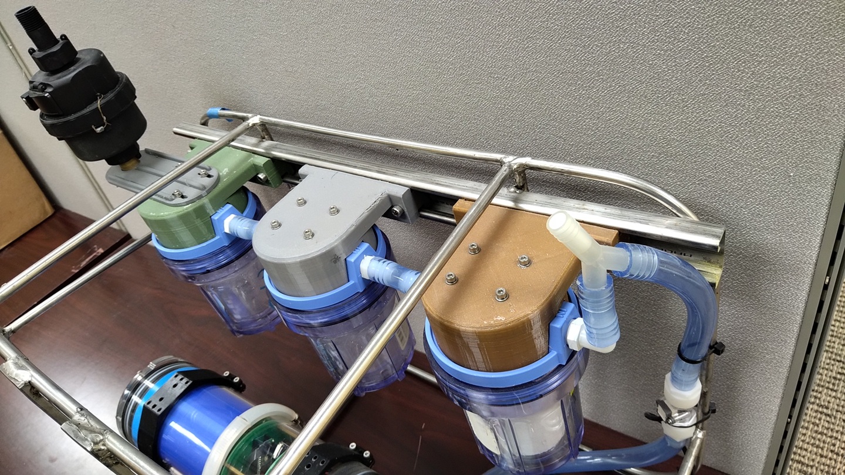
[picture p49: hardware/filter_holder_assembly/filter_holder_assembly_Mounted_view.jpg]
         <td></td>
      </tr>
       <tr>
         <td>filter_holder_assembly Full view</td>
         <td>filter_holder_assembly mounted to frame_assembly</td>
      </tr>
   </table>
   
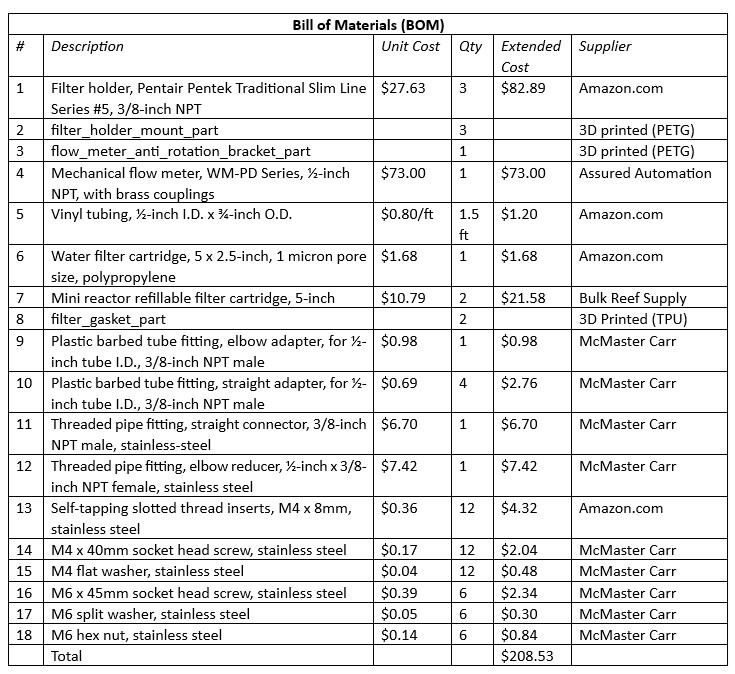
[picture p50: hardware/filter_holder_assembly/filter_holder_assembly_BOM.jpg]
<P></P>

### Assembly (approximate time: 30 minutes)
1.	Expand the diameters of the four filter holder mounting holes to accommodate the self-tapping threaded inserts using a ¼-inch drill bit to a minimum depth of 10 mm (four holes per filter holder). Then screw in the self-tapping inserts until flush with top of filter holder.
<P>
  <table>
<tr>
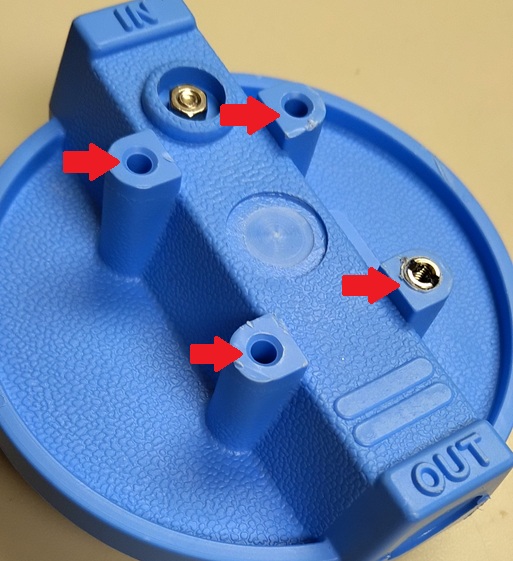
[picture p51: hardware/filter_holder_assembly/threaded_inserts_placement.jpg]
  <td align=center>
  </td>
</tr>
    <tr>
  <td align=center>Red arrows indicate locations of holes for threaded insert placement.
  </td>
</tr>
  </table>
</P>
<P>2.	For the first two filter holders in series:  First, screw four plastic barbed hose fittings into the filter holder inlets / outlets using Teflon thread-sealing tape. Then, attach the filter holders to filter_holder_mount_parts using M4x40 mm stainless steel socket head screws and washers (four screws for each holder).
<p>3.	For the third filter holder: First, screw the straight, stainless steel male connector into the female elbow reducer, and screw the straight connector into the filter holder outlet using Teflon tape. Next, align the slots in the flow_meter_anti_rotation_bracket_part with the mounting holes in the filter_holder_mount_part, then attach those parts to the filter holder using four M4x40 mm screws and washers. Finally, attach the flowmeter to the elbow reducer (the flowmeter should be mounted vertically). See photo below.
   <P>
  <table>
<tr>
  <td align=center>
  </td>
</tr>
    <tr>
  <td align=center>Close-up showing position of flowmeter_anti_rotation_bracket_part.
  </td>
</tr>
  </table>
</P>
<P>4.	The filter holders can now be attached in series using vinyl tubing and mounted to the strut channel of the frame_assembly using six M6x45 mm stainless steel socket head screws, split washers, and hex nuts.
<P>5.	Then, use vinyl tubing to connect the outlet of the pump_unit_assembly to the inlet of the first filter holder (barbed fittings on each).
<P>If you are using the Bulk Reef Supply refillable filter cartridges, we found that the included gasket does not always provide a sufficient seal against the inside top of the Pentek filter holder. For this reason, we designed a slightly larger replacement gasket (filter_gasket_part), which can be 3D printed (see photos below).</P>   
<P>
  <table>
    <tr>
      <td>
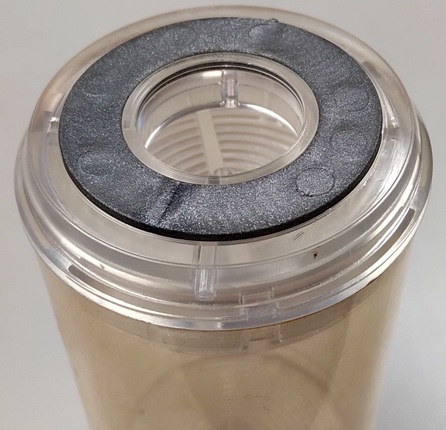
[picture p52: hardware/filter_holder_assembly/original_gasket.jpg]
        
      </td>
      <td>
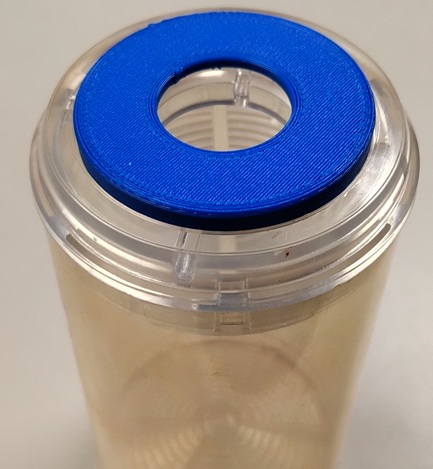
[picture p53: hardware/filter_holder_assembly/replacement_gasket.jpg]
        
      </td>
    </tr>
    <tr>
      <td align=center>
        Refillable filter cartridge with original gasket.
      </td>
       <td align=center>
        Cartridge with replacement gasket
      </td>
    </tr>
  </table>
</P>

### 3D Printed Parts
We use PETG filament with 100% infill to produce the filter_holder_mount_part and the flow_meter_anti_rotation_bracket_part. The filter_gasket_part is printed with the more flexible TPU filament. 

The 3D models including .STEP and .STL files are available in the <a href="3D_models/">3D Models directory</a>.
<P>
  <table>
    <tr>
      <td>
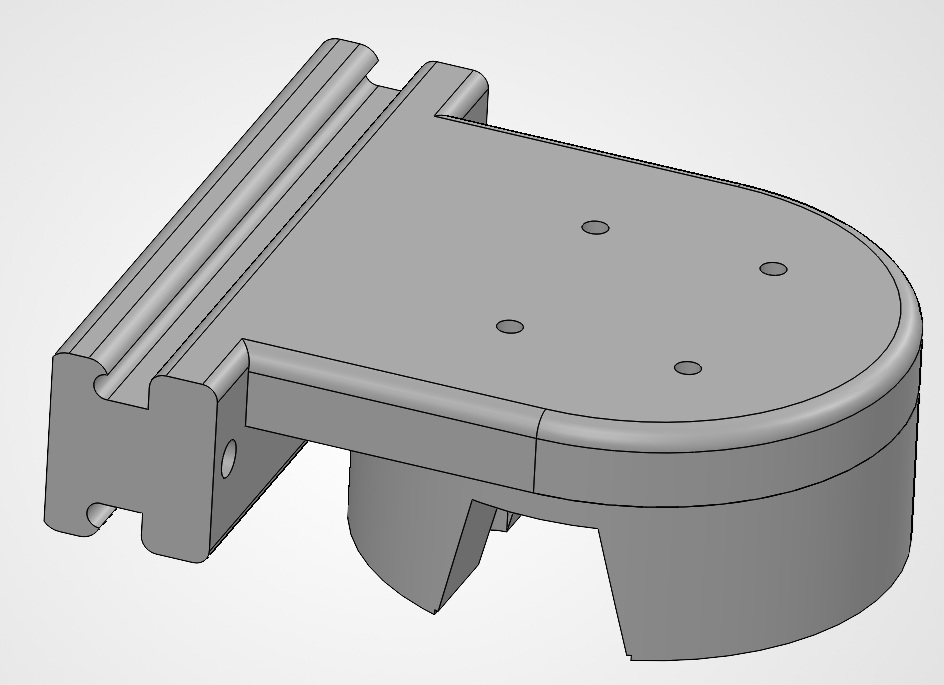
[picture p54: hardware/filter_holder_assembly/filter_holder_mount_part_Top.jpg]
        
      </td>
      <td>
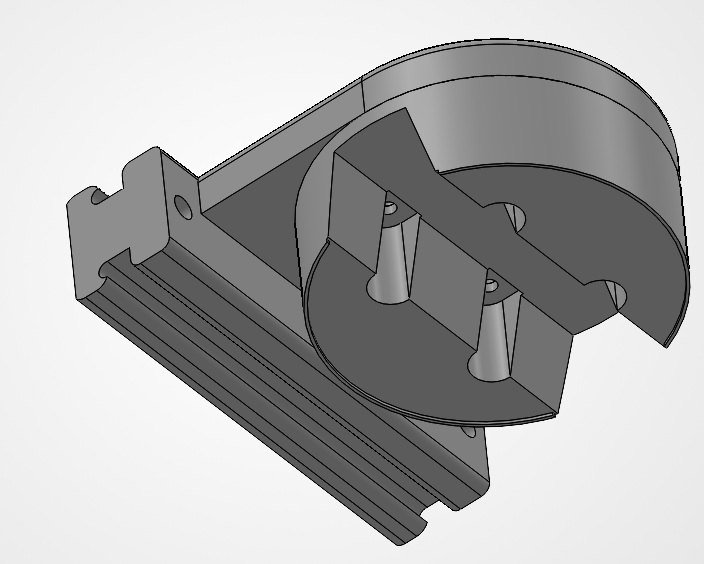
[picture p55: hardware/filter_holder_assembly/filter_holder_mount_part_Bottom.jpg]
        
      </td>
    </tr>
    <tr>
      <td align=center colspan=2>
        filter_holder_mount_part
      </td>
    </tr>
  </table>
</P>

<P>
  <table>
    <tr>
      <td>
        
      </td>
    </tr>
    <tr>
      <td align=center>
        flow_meter_anti_rotation_bracket_part
      </td>
    </tr>
  </table>
</P>
<P>
  <table>
    <tr>
      <td>
        
      </td>
    </tr>
    <tr>
      <td align=center>
        filter_gasket_part
      </td>
    </tr>
  </table>
</P>

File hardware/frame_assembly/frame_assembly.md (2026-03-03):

# frame_assembly
<P>The frame, or cage, is constructed of welded 3/8-inch diameter corrosion resistant 316 stainless 
steel rods.  Attached to this structure are a) a ¼-inch thick stainless-steel plate for mounting the 
watertight enclosure and pump unit, b) a stainless-steel strut channel for mounting the filter 
holders, and c) four ¼-inch thick stainless plates for mounting the wire clamps.  The dimensions of 
the frame are 24 x 12 x 16 inches.</P>

<table>
  <tr>
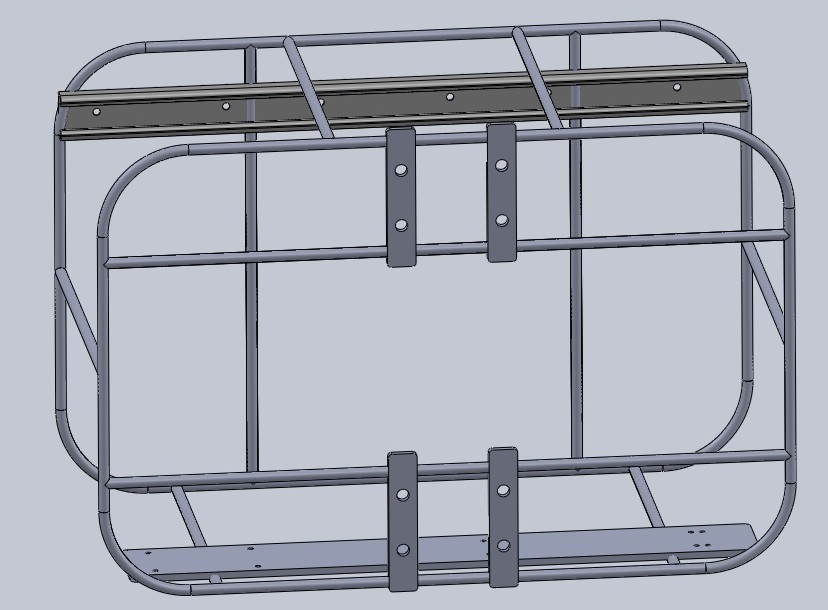
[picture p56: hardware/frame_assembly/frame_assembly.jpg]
    <td></td>
  </tr>
  <tr>
    <td align=center>frame_assembly</td>
  </tr>
 </table>

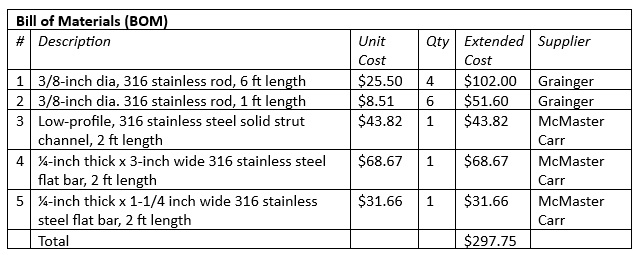
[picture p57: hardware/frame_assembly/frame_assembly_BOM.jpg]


### Assembly (approximate time: 4 hours):  
1. Prepare stainless steel rod members (dimensions given in figure below).  Bends are 3
inch radius. Grind ends to a point for welding. 
<table>
  <tr>
    <td></td>
  </tr>
  <tr>
    <td align=center>Sketch of frame showing dimensions (inches) of 3/8-inch stainless steel rod members.</td>
  </tr>
 </table>
2. Weld members according to figures.
<table>
  <tr>
    <td></td>
  </tr>
  <tr>
    <td align=center>Stainless steel rods clamped for welding.</td>
  </tr>
 </table>
3. Trim the 3 x 24 inch stainless steel flat bar down to 22-inches in length.  Then place 12 x M4 clearance holes in the stainless steel base plate as shown in the figure below. The eight holes on the left are for mounting the two watertight enclosure clamps, and the four holes on the right are for mounting the pump_unit. Next, polish the plate with a flap disk, and then weld the base plate to two lower cross members.
<p>
  <table>
  <tr>
    <td></td>
  </tr>
  <tr>
    <td align=center>Sketch of base plate with M4 clearance hole placement.</td>
  </tr>
 </table>
4. Place 8x M6 clearance holes for filter holder mounts in strut channel as shown in figure 
below. Weld the channel to four vertical rods at back of frame.
<table>
  <tr>
    <td></td>
  </tr>
  <tr>
    <td align=center>Sketch of strut channel with placement of M6 holes for filter holder mounts. </td>
  </tr>
 </table>
5. Prepare the wire clamp mounts by cutting the ¼-inch by 1 1/4-inch stainless steel plate into 
5-inch lengths (4 pieces needed). Place two M10 clearance holes in each of the four wire 
clamp mounts as shown in figure below. Weld each mount to two horizontal rod 
members as shown in figure above.
<table>
  <tr>
    <td></td>
  </tr>
  <tr>
    <td align=center>Sketch of wire clamp mount with M10 clearance hole placement.</td>
  </tr>
 </table>

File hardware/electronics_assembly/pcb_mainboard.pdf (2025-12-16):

PCB: Mainboard

The Mainboard contains the Teensy 4.1 microprocessor unit and direct connections for components including, PWM signal to the BLDC motor electronic speed controller (ESC), input from the flow sensor (Flow), pressure sensor (Pressure), and current sensor (Current Sensor), and output to the red LED indicating ready to run (LED1) and to the green LED indicating the start timer (LED2). A coin cell battery holder (BAT1) allows Teensy’s RTC to keep time while the unit is disconnected from external power. Teensy’s built-in microSD card allows for data logging. Teensy’s microUSB adapter is connected to a USB-A connector on the Mainboard, allowing external connection to a PC via the bulkhead connector on the end cap. The Mainboard is mounted on a tray between the end cap and Battery Holder Bottom with brass spacers through the four mounting holes.

Note: Pins Int2 is unused as of the pump’s current state.


PCB: Mainboard (Front) | PCB: Mainboard (Back)

Bill of Materials (BOM)
# | Description | Loc. | Cost (USD) | Qty | Supplier

1 | Teensy 4.1 microcontroller with pins | Teensy 4.1 | $40.00 | 1 | Amazon.com
2 | Single row PCB female pin headers, 2.54 mm pitch | Teensy 4.1 | $0.05 | | Amazon.com
3 | Coin cell PCB mount battery holder | BAT1 | $0.60 | 1 | Amazon.com
4 | JST-XH 2-pin PCB mount connector, 2.54 mm pitch | ESC, LED1, LED2, Int1, Switch | $0.03 | 5 | Amazon.com
5 | JST-XH 3-pin PCB mount connector, 2.54 mm pitch | Flow, Int2 | $0.03 | 2 | Amazon.com
6 | JST-XH 4-pin PCB mount connector, 2.54 mm pitch | USB In, Pressu re | $0.03 | 2 | Amazon.com
7 | Coin cell 3V battery (e.g. CR2032, CR2025, CR2015) | | $0.60 | 1 | Amazon.com
8 | 32 GB microSD memory card | | $4.00 | 1 | Amazon.com
9 | USB Type A Female Socket USB Board connector, 2.54mm pitch | USB A | $0.70 | 1 | Amazon.com
10 | LM2596 DC-DC adjustable Buck converter step-down voltage regulator module | Regula tor | $1.25 | 1 | Amazon.com
11 | Screw terminal block connector, 2-pin, THT, 5 mm pitch | Batter y | $0.15 | 2 | Amazon.com
12 | INA219 High Side DC Current Sensor Breakout - 26V +-3.2A Max - Stemma QT | Curren t Sensor | $16.26 | 1 | Amazon.com

Total Cost: $64.03

Assembly (approximate time: 30 minutes):

Prep Note:
- Solder pins onto all four vias on back side of voltage regulator.
- Remove terminal block included in current sensor and replace with pins, and solder the other six pins onto the remaining vias.

Main Assembly:

All components mount to the top of the Mainboard.

1. Insert pin headers, battery holder, JST-XH connectors, screw terminal block connectors, voltage regulator, and current sensor to PCB board.
2. Solder all pins.
3. Insert Teensy 4.1 into headers, insert microSD card, and insert battery.


Assembled PCB: Mainboard (Front) | Assembled PCB: Mainboard (Back)

Teensy 4.1 Pin Assignments
Pin | Wire – color (function) | Color (function)
23 | ESC | White
GND | ESC | Black (GND)
29 | Flow sensor | Yellow
3.3V | Flow sensor | Red (VIN)
GND | Flow sensor | Black (GND)
3.3V | BAR30 | Red (VIN)
19 | BAR30 | Green (SCL)
18 | BAR30 | White (SDA)
GND | BAR30 | Black (GND)
17 | Red LED | Red (VIN)
GND | Red LED | Black (GND)
16 | Green LED | Green (VIN)
GND | Green LED | Black (GND)
41 | Switch 2 | Blue
3.3V | Switch 2 | Blue (VIN)
40 | INT2*
3.3V | INT2*
GND | INT2*

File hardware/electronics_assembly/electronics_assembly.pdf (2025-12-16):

electronics_assembly

The Electronics Assembly consists the watertight enclosure with end cap mounted sensors, indicators, and penetrators, and the internal electronic and power components (i.e., assembled PCB and batteries). The assembly is secured to the frame’s Base Plate with watertight enclosure clamps.

[Note: Alternate Version] The instructions and files here are for the 100mm (4-inch) diameter enclosure. Assembly for projects using a 130mm (5-inch) tube


Pump Unit - exploded view
(Not shown: power cord & O-ring)


Pump Unit 3D printed parts

Assembly (approximate time: 2 hours):

[Recommended tools and supplies: Blue Robotics WetLink Bulkhead Wrench, adjustable wrench, bench vise, wire strippers, ratcheting crimping tool for JST connectors]

1. Mount the endcaps to the O-ring sealing flanges using the included face seal O-ring and end cap screws.
2. Prepare each wire by trimming it to ≈ 10cm, stripping the end, and crimping on a female pin connector.
3. Prepare Flow sensor wire by removing wires connected to the flow sensor module and replacing it with ≈ 65cm of PUR Subsea 3 conductor cable.

Note: The assembled 3-pin and 4-pin connectors will not fit through the M10 end cap holes. Therefore, it is recommended not to insert the wires into the plastic body until the component or penetrators has been mounted to the end cap.

4. Mount the following components to the M10 x10 hole end cap: WetLink penetrators for the motor and flow sensor, Bar30 pressure sensor, red and green LEDs, two switches, Cobalt bulkhead connector (USB), pressure relief valve, and a blank penetrator.


M10 x10 hole end cap with mounted components.

5. Insert each wire into the appropriate JST connector body.

JST XH Connector Wiring Guide

ESC | Switch,
T_Switch

Red LED Green
LED

Flow
Sensor
Bar30 | USB

6. Plug in the following components to the front of the Assembled Mainboard: red and green LEDS, two switches, Bar30 Pressure sensor, Cobalt connector wires (USB connection), Flow sensor, and ESC connector.
7. Insert the ESC power leads (thick red and black wires) into the front screw terminal block, and tighten down.
8. Insert the three banana connector male leads from the E200 motor into the matching female leads from the ESC.
9. Screw four M3x60mm brass hex spacers into mounting holes in the sealing flange.
10. Solder the banana connectors to the three conductors of the motor cable. Then apply heat shrink tubing to the connection.
11. Attach the motor to Pump Base with four M3 x 8mm screws.
12. Place the Pump Body over the motor.
13. Attach impeller to motor with two M3 x 8mm screws.
14. Insert O-ring into groove in Pump Body.
15. Seat the Pump Head over the Impeller and onto Pump Body.
16. Secure Pump Head to Pump Base with four sets of ¼ inch screws, washers, and wingnuts.

Bill of Materials (BOM)
# | Description | Cost (USD) | Qty | Supplier

1 | Watertight enclosure tube, 100 mm dia., aluminum | $410.00 | 1 | Blue Robotics
2 | O-ring sealing flange, 100 mm dia. | $48.00 | 2 | Blue Robotics
3 | End cap, blank, 100 mm dia., aluminum | $32.00 | 1 | Blue Robotics
4 | End cap, 10 x M10 holes, 100 mm dia., aluminum | $40.00 | 1 | Blue Robotics
5 | Pressure relief valve | $30.00 | 1 | Blue Robotics
6 | WetLink penetrator, blank, M10 thread | $6.00 | 1 | Blue Robotics
7 | Switch | $26.00 | 2 | Blue Robotics
8 | Subsea LED indicator, red | $16.00 | 1 | Blue Robotics
9 | Subsea LED indicator, green | $16.00 | 1 | Blue Robotics
10 | Bar30 pressure sensor | $85.00 | 1 | Blue Robotics
11 | Cobalt series bulkhead connector, 4-pin | $55.00 | 1 | Blue Trail Engineering
12 | JST XH-2P connector plug, female (2-pin) | $0.03 | 4 | Amazon.com
13 | JST XH-4P connector plug, female (4-pin) | $0.03 | 2 | Amazon.com
14 | Brass hex standoff spacer, M3 x 12mm +6mm, male to female | $0.45 | 4 | Amazon.com
15 | Brass hex standoff spacer, M3 x 30mm +6mm, male to female | $0.40 | 4 | Amazon.com
16 | Brass hex standoff spacer, M3 x 50mm +6mm, male to female | $0.65 | 8 | Amazon.com
17 | Brass hex standoff spacer, M3 x 60mm +6mm, male to female | $0.50 | 8 | Amazon.com
18 | Brass screws, M3 x 6mm, Phillips head | $0.02 | 4 | Amazon.com
19 | 22 AWG silicone insulated wire | $13.69 | 1 | Amazon.com
20 | Crimp connectors
21 | USB-A to Micro USB cable, 15cm, 90 degrees angled up | $14.00 | 1 | Amazon.com
22 | Battery Holder Tube | | 1 | 3D Printed (PLA)
23 | Batteries, c-cell | $1.00 | 14 | Amazon.com
24 | Flow Sensor Assembly | $9.95 | 1 | Amazon.com
25 | PUR Subsea Cable – Lumen/Gripper Cable (3 conductor, 22 AWG) | $16.00 | 1 | Blue Robotics
26 | M200 Motor | 185.00 | 1 | Blue Robotics
27 | Pump Body, Base, Head, Impeller | | 1 | 3D Printed (Resin)

Total Cost: $1,005.72

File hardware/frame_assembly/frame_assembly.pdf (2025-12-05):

frame_assembly

The frame, or cage, is constructed of welded 3/8-inch diameter corrosion resistant 316 stainless steel rods. Attached to this structure are 1) a ¼-inch thick stainless-steel plate for mounting the watertight enclosure and pump unit, 2) a stainless-steel strut channel for mounting the filter holders, and 3) ¼-inch thick stainless plates for mounting the wire clamps. The dimensions of the frame are 24 x 12 x 16 inches.


Assembly (approximate time: 4 hours):
1. Prepare stainless steel rod members (dimensions given in figure below). Bends are 3-inch radius. Grind ends to a point for welding.
2. Weld members according to figures.

Frame_assembly

Bill of Materials (BOM)
# | Description | Unit Cost | Qty | Extended Cost | Supplier

1 | 3/8-inch dia, 316 stainless rod, 6 ft length | $25.50 | 4 | $102.00 | Grainger
2 | 3/8-inch dia. 316 stainless rod, 1 ft length | $8.51 | 6 | $51.60 | Grainger
3 | Low-profile, 316 stainless steel solid strut channel, 2 ft length | $43.82 | 1 | $43.82 | McMaster Carr
4 | ¼-inch thick x 3-inch wide 316 stainless steel flat bar, 2 ft length | $60.50 | 1 | $60.50 | Grainger
5 | ¼-inch thick x 1-inch wide 316 stainless steel flat bar, 2 ft length | $20.17 | 1 | $20.17 | Grainger
| Total | | | $278.09


Sketch of frame showing dimensions (inches) of 3/8-inch stainless steel rod members.

3. Place 12 x M4 clearance holes in stainless steel base plate as shown in figure below. Weld the base plate to two lower cross members.

Sketch of base plate with M4 clearance hole placement.
4. Place 8x M6 clearance holes for filter holder mounts in strut channel as shown in figure below. Weld the channel to four vertical rods at back of frame.


Sketch of strut channel with placement of M6 holes for filter holder mounts.

5. Prepare the wire clamp mounts by cutting the ¼-inch by 1-inch stainless steel plate into 5-inch lengths (4 pieces needed). Place two M10 clearance holes in each of the four wire clamp mounts as shown in figure below. Weld each mount to two horizontal rod members as shown in figure above.


Sketch of wire clamp mount with M10 clearance hole placement.
